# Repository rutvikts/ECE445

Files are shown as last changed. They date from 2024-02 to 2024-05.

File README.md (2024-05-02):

# ECE 445
UIUC ECE 445 - Senior Design Project Repository

# Project Details
## Oxygen Delivery Robot

Team Members:
- Rutvik Sayankar (rutviks2@illinois.edu)
- Aidan Dunican (dunican2@illinois.edu)
- Nazar Kalyniouk (nazark2@illinois.edu)

## Problem

Children's interstitial and diffuse lung disease (ChILD) is a collection of diseases or disorders. These diseases cause a thickening of the interstitium (the tissue that extends throughout the lungs) due to scarring, inflammation, or fluid buildup. This eventually affects a patient’s ability to breathe and distribute enough oxygen to the blood.

Numerous children experience the impact of this situation, requiring supplemental oxygen for their daily activities. It hampers the mobility and freedom of young infants, diminishing their growth and confidence. Moreover, parents face an increased burden, not only caring for their child but also being directly involved in managing the oxygen tank as their child moves around.

## Solution

Mobile oxygen delivery is a mostly untapped market for users both elderly and young. This project details a prototype design for a mobile oxygen delivery robot. We utilize a three-wheeled omnidirectional drivetrain, ultra-wideband triangulation, computer vision, and a simple Roomba-style bumper system. We remove ourselves from the context of dealing with oxygen-related tubing as swivel solutions already exist and focus on the issue of creating a robot that can autonomously and efficiently move an oxygen tank around in an indoor space.

### Final Robot Design
<p align="center">
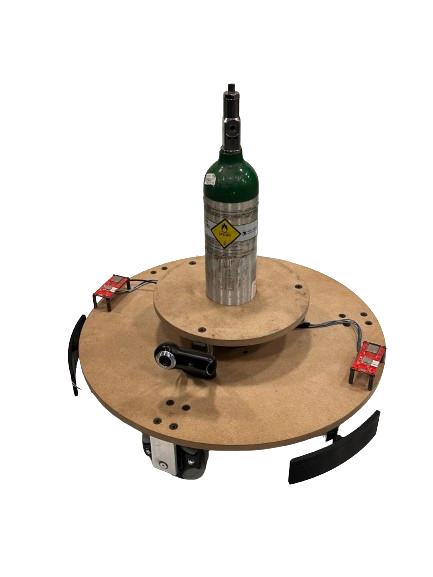
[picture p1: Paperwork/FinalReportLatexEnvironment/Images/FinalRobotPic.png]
  
</p>

### Final Robot Wiring (Underside)
<p align="center">
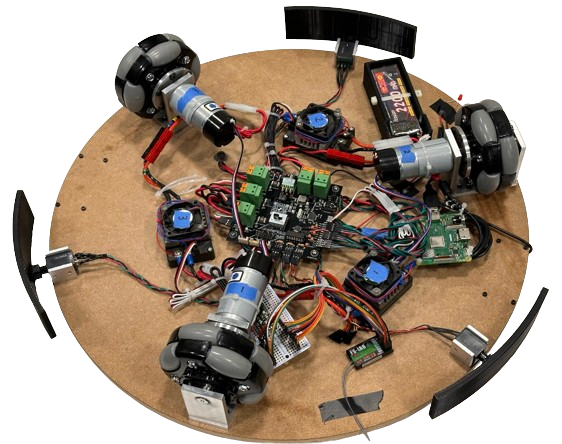
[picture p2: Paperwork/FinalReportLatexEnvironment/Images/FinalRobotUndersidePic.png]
  
</p>

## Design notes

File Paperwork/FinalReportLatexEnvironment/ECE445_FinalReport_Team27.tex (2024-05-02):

\documentclass{report}

\usepackage[top=1.5in,left=1.5in,bottom=1.5in,right=1.5in]{geometry}
\usepackage{amsmath}
\usepackage{bookmark}
\usepackage{listings} % for including nicely formatted code
\usepackage{array} % Included to solve invalid char in Tables declaration
\usepackage{graphicx} % to insert images
\graphicspath{{../pdf/}{/Users/rutviksayankar/Repos/ECE445_SP24/Paperwork/FinalReportLatexEnvironment/Images}} % setting up path for image storage

\usepackage{hyperref} % allows table of contents to be clickable to sections
\hypersetup{
    colorlinks,
    citecolor=blue,
    filecolor=blue,
    linkcolor=blue,
    urlcolor=blue
}

% Setting color formatting for Python code
\lstset{
    language=Python,
    frame=tb,
    basicstyle=\fontsize{8}{10}\ttfamily,
    keywordstyle=\color{blue},
    stringstyle=\color{red},
    commentstyle=\color{green},
    morecomment=[l][\color{magenta}]{\#},
}

% Setting color formatting for C code
\lstset{
    language=C,
    basicstyle=\fontsize{8}{10}\ttfamily,
    keywordstyle=\color{blue},
    stringstyle=\color{red},
    commentstyle=\color{magenta},
    morecomment=[l][\color{magenta}]{\#},
    frame=tb,
    numbers=left,
    % numberstyle=\tiny\color{gray},
    breaklines=true,
    showstringspaces=false,
}

% This section redefines the chapter headings, this allows us to remove the implicit "Chapter #" that comes before a provided chapter title.
\makeatletter
\def\@makechapterhead#1{%
  \vspace*{20\p@}%
  {\parindent \z@ \raggedright \normalfont
    \ifnum \c@secnumdepth >\m@ne
      %\if@mainmatter
        %\huge\bfseries \@chapapp\space \thechapter
        \Huge\bfseries \thechapter.\space%
        %\par\nobreak
        %\vskip 20\p@
      %\fi
    \fi
    \interlinepenalty\@M
    \Huge \bfseries #1\par\nobreak
    \vskip 40\p@
  }}
\makeatother

\title{ECE 445: Senior Design Project Laboratory \\ Final Report \\ Oxygen Delivery Robot} % Sets article title

\author {
    \textbf{Team 27} \\ 
    \textit{Sayankar, Rutvik}\\
    \textit{rutviks2@illinois.edu} \\
    \hfill \\ 
    \textit{Dunican, Aidan}\\
    \textit{dunican2@illinois.edu} \\
    \hfill \\ 
    \textit{Kalyniouk, Nazar}\\
    \textit{nazark2@illinois.edu} \\
    \hfill \\ 
    \textbf{Teaching Assistant} \\ 
    \textit{Subramaniam, Selva} \\
    \textit{ss170@illinois.edu} 
} 
\date{\today} % Sets date for date compiled

% The preamble ends with the command \begin{document}
\begin{document}
    \maketitle % creates title using information in preamble (title, author, date)

    \begin{abstract}
        Mobile oxygen delivery is a mostly untapped market for users both elderly and young. This report details a prototype design for a mobile oxygen delivery robot. We utilize a three wheeled omni-directional drivetrain, ultra wideband triangulation, computer vision, and a simple Roomba style bumper system. We remove ourselves from the context of dealing with oxygen related tubing as swivel solutions already exist and focus on the issue of creating a robot that can autonomously and efficiently move an oxygen tank around in an indoor space.
    \end{abstract}
    
    \pagebreak
    \tableofcontents % creates table of contents
    \pagebreak

    \chapter{Introduction}
    \section{Project Overview}
    Children's interstitial and diffuse lung disease (ChILD) is a collection of diseases or disorders. These diseases cause a thickening of the interstitium (the tissue that extends throughout the lungs) due to scarring, inflammation, or fluid buildup \cite{ChILD-2022}. This eventually affects a patient’s ability to breathe and distribute enough oxygen to the blood. Numerous children experience the impact of this situation, requiring supplemental oxygen for their daily activities. It hampers the mobility and freedom of young children, diminishing their growth and confidence. Moreover, parents face an increased burden, not only caring for their child but also having to be directly involved in managing the oxygen tank as their child moves around.

    Given the absence of relevant solutions in the current market, our project aims to ease the challenges faced by parents and provide young children the freedom to explore their surroundings without worry. As a proof of concept for an affordable solution, we propose a three wheeled omni-directional mobile robot capable of supporting a filled M-6 oxygen tank. We plan to implement two localization subsystems to ensure redundancy and enhance child safety. The first subsystem utilizes Ultra-Wideband (UWB) transceivers for triangulating the child's location relative to the robot in indoor environments, this is similar to how Apple AirTags triangulate their location relative to an iPhone \cite{airtag_uwb} (although AirTags use a combination of UWB and Bluetooth triangulation \cite{airtag_ble}). The second subsystem makes use of a desktop web camera which streams video to a Raspberry Pi where it will leverage open-source object tracking libraries to improve our directional accuracy in tracking a child. The final subsystems will focus on close range object detection.

    \newpage

    \section{Block Diagram}
    \begin{figure}[ht!]
      \centering
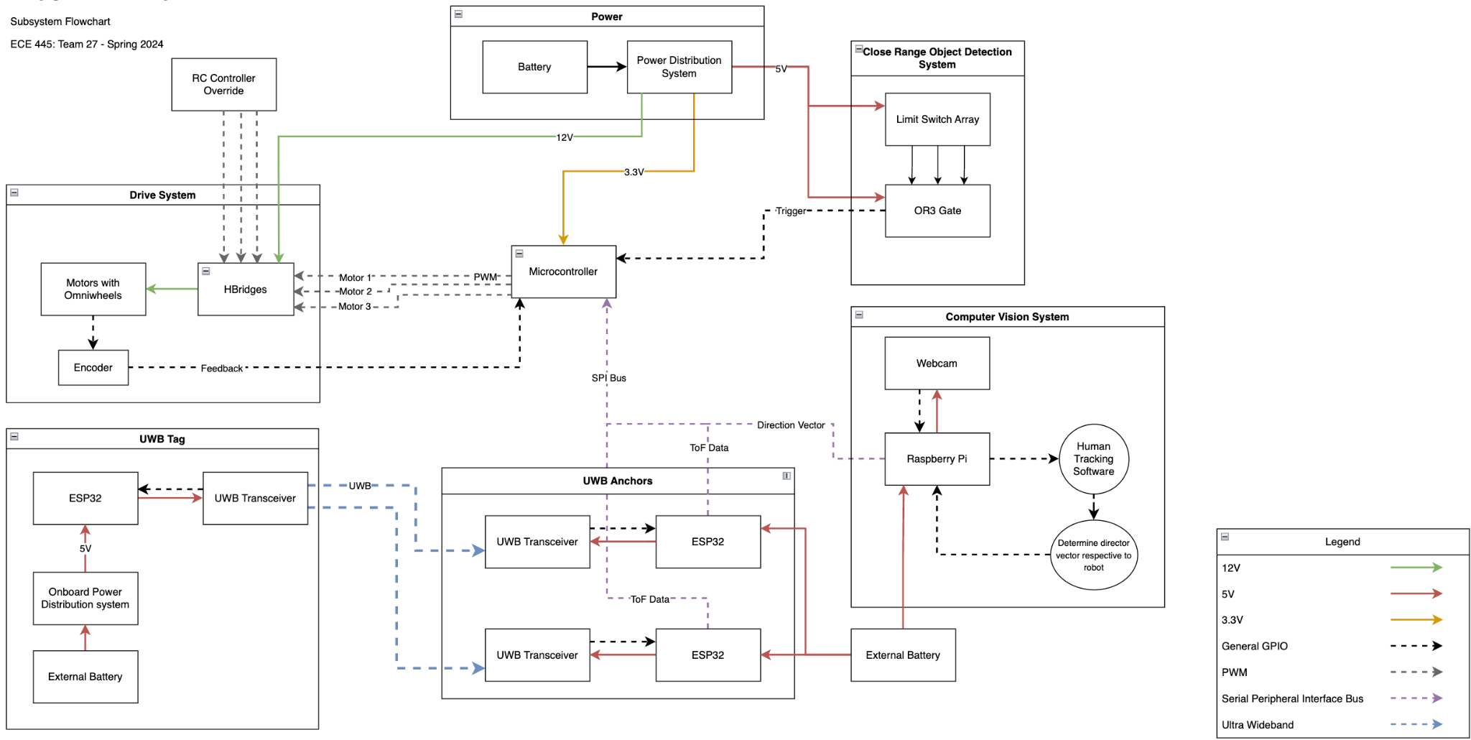
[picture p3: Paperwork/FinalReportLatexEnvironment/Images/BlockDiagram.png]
      
      \caption{High Level Block Diagram}
      \label{fig:BlockDiagram}
  \end{figure}

    \subsection{Omniwheel Drivetrain System}
    We utilize a three wheeled omni-directional wheel drive train. In software we make use of simple matrix multiplication (detailed in section \ref{sec:Omniwheel-InverseKinematics}) to derive individual wheel speeds given that we know where we want to go in Cartesian space.

    \subsection{Ultra-Wideband Triangulation System}
    This system makes use of UWB transceivers in order to triangulate location in an indoor space with high accuracy. The goal was to be able to locate the user in an indoor environment where there maybe be interference with other bluetooth or wifi signals. 
    
    \subsection{Close Range Object Detection System}
    The Close Range Object Detection subsystem makes use of limit switches with bumpers attached to them arranged in a ring around the robot that will detect when it encounters an object in its path. The goal of this system is to halt the robot and any further movement when a limit switch is pressed. This enhances the safety of the robot, particularly in environments with children. With the expectation that the robot will be utilized inside spaces such as a living room which might have toys scattered around due to younger children being present. To limit the scope of the project we want the robot to simply stop movement upon collision with any object in it's path and have either the user or a someone supervising come in and clear the area before the robot is to be used again.
    
    \subsection{Computer Vision System}
    The Computer Vision subsystem was incorporated into our design to ensure redundancy and robustness. By having a sensor fusion between this and the UWB subsystem, we can ensure that the robot follows the child as desired and add an extra layer of redundancy and safety to our design. The performance requirements of this subsystem are that this subsystem will initiate a corrective measure to the STM32 microcontroller if the child deviates too far from the center of the input frame. Specifically, this system focuses on the degrees away from the center the user currently is. Between the start of this design and the end, nothing was changed in the block level of this subsystem.
    
    \subsection{Control System}
    This system is purely regarding how the STM32 microcontroller interacts and controls all our peripheral devices.
    
    \subsection{Power System}
    The power system of our robot was designed to take a 12V input and regulate it down to the 5V and 3.3V rails that will be used by all devices on our PCB. Specifically, for our 3.3V rail we needed to ensure a clean supply as it would be powering our STM32 microcontroller, which will be generating all of our PWM signals and reading a lot of timer related signals for which a clean 3.3V is preferred.

    \chapter{Design}
    \section{Design Procedure}

    \subsection{Omniwheel Drivetrain System}
    \label{sec:Omniwheel-DesignProcedure}

    We utilize a three wheeled omni-directional wheel drive train. Chosen mainly due to the cost benefit over a similar four wheeled drive train. This type of system is susceptible to drift in the form of yaw, therefore we made sure to include feedback from encoders back into our STM32 microcontroller to allow for drift compensation.

    \subsection{Ultra-Wideband Triangulation System}
    Our initial design discussion was regarding the type of wireless indoor localization we want to design. Immediately, two types of communication came to mind: UWB and BLE. Ultimately, we chose UWB over BLE due to the following benefits:

    \begin{itemize}
      \item Data transmission: UWB can transmit more data than Bluetooth Low Energy
      \item Accuracy: UWB can more accurately measure distance and determine position because it uses wideband radio waves and higher frequency bands
      \item Interference resistance: UWB is less likely to be affected by interference and obstructions
    \end{itemize}

    \subsubsection{Localization Algorithms} 
    To break it down simply, our goal was to find out the location of a user relative to our robot. We assume the user and robot will be in a valid location in real world space, and therefore can just focus on the user's location relative to our robot.

    To localize the user, we need to create a triangle of known lengths with vertices defined by the UWB transceivers. To obtain the lengths of each side we need to perform some ranging between the tag transceiver (the transceiver which the user will have) and the anchor transceivers (which are mounted onto the robot). With the anchors being a set 18" apart (the minimum as required by the DW3000 ICs we were using), we only needed the remaining two sides of our triangle.

    There are two ways to range between UWB transceivers. The first is to use Time of Flight (ToF). ToF is a positioning method based on two-way ranging. That means the tag needs to send and receive signals from the anchor several times and then the flight time of the signal between the anchor and the tag can be measured, because radio waves travel at the speed of light, we can calculate the distance between the tag and each anchor given that we know how long it took for a signal to travel between them. Secondly, Time Difference of Arrival (TDoA) is localization based on comparing the time difference between signals and each anchor and this technique requires an accurate time synchronization function. When using the TDoA method, the UWB tag will send out a poll message, and all the nearby UWB anchors will receive it and record the arrival time. Because the location of anchors is different, they will not receive the message at the same time. We can use these time differences to determine the tag’s location.

    Implementing an accurate time synchronization function between all of our transceivers increases the complexity of the project ten-fold therefore we decided to use a ToF based ranging method to calculate the distance between each anchor and the tag device.
    
    \subsection{Close Range Object Detection System}

    This system is the simplest but definitely required some debate in terms of how we wanted it implemented. We debated between two main types of detection: simple limit switches or ultrasonic sensors. Limit switches don't require explanation, you activate a switch and a signal goes high. The only struggle here would be finding a limit switch that would be suitable for our needs. The alternative was ultrasonic detection which would have required us to use a much larger number of sensors and which would have been much more sensitive. The reason we decided to use limit switches was that they would only stop the robot when an object collides with it. In addition, limit switches allow us to make a 360-degree bumper for the robot with only 3 switches, which would fill in the gap between each wheel. To design the subsystem we decided to go with the 3 Honeywell 101SN11 limit switches as they were the best available limit switch in the ECE Self-service center (put simply, it was the only limit switch that could take any sort of impact without damage). One of the major issues we had when designing this subsystem was how to get the Honeywell limit switches to work. Seeing as these limit switches have since been discontinued, finding proper documentation on them proved to be difficult. We discovered that the output to the limit switches needed a 10k pull-up resistor in order to drive the output high when the limit switch is inactive. This was all thanks to a helpful ebay seller who provided a simple explanation on the function of some old limit switches he was selling (\url{www.ebay.com/itm/333999755279 }).
    
    \subsection{Computer Vision System}
    Alternate approaches to incorporating person detection besides using a Haar cascade which we ultimately chose are as follows.
    
    \begin{itemize}
      \item Histogram of Oriented Gradients (HOG)
      \item You Only Look Once (YOLO)
      \item Single Shot MultiBox Detector (SSD)
    \end{itemize}
    
    Haar cascade was chosen for our final implementation as it is simpler to implement than conventional deep-learning models. It contains pre-trained full body models, a large stepping stone which would be required for our project. For the Haar cascade algorithm, a pre-trained model that detects full bodies is used. Once the body is detected, a bounding box is drawn around the body. The center point of this box and the center point of the screen are compared and this determines how far off the center the body is.
    
    \subsection{Control System}

    The details of the control system during design were fairly simple. It mainly consisted of choosing a microcontroller and deciding what pins to assign where. We were limited by what was provided by the ECE supply center, we decided to go with the F103 line of STM32 chips as we believed it had the perfect amount of GPIO and timer pins required for our robot. Our final pin assignments are shown in figure \ref{fig:STM32Pinout}.
    \\
    \\
    We required individual timers for the following:
    \begin{itemize}
      \item PWM output to motors (can all be synchronized therefore only need one timer)
      \item Motor 1 Encoder feedback
      \item Motor 2 Encoder feedback
      \item Motor 3 Encoder feedback
    \end{itemize}
We required GPIO for the following:

    \begin{itemize}
      \item Limit switch bumper input
      \item USB lines
      \item SPI bus
      \item Chip select for 3 peripherals on the SPI bus
      \item High Speed External Crystal Oscillator input and output.
      \item Programmer pins
    \end{itemize}
    
    \subsection{Power System}

    In our initial power design we had four requirements:

    \begin{itemize}
      \item Supply a max of $9~A$ at $12~V$ per motor therefore $27~A$ at $12~V$
      \item Supply $5~V$ to supply around $3.5~A$ line to power items like a Raspberry Pi running computer vision software, and two ESP32 boards that power the UWB transceiver anchors on the robot, and some other miscellaneous 5V powered ICs throughout our PCB.
      \item Supply $3.3~V$ at $< 80~mA$ for our STM32.
    \end{itemize}

    We initially began with separate buck converters for each of our power rails. This original design took up lots of space on our PCB and was unnecessary as we only needed one $5~V$ line rated for higher current. After realizing that our selection of ESP32 boards and Raspberry Pi's do not have the option of power delivery through GPIO pins, we decided to use an external battery pack to supply them power. But we opted to leave our higher current buck converter in the design to leave headroom for the possibility of delivering power to our Raspberry Pi and two ESP32 boards in the future. This led us to designing our final power system which consisted of a $12~V$ to $5~V$ buck converter rated for up to $6~A$. This was followed with a $5~V$ to $3.3~V$ LDO to supply the power to our $3.3~V$ line. The reason we opted to go with an LDO for the 3.3v was because it was supplying power to the microcontroller which due to its sensitivity needed to be at a stable $3.3~V$ ideally without much noise. By opting to go with an LDO we were able to lower the noise floor and improve the line regulation of the supply going to the STM32 and hopefully improve the analog performance of our microcontroller.

    To further ensure the performance of the our analog pins in our microcontroller we decided to make use a ferrite bead which suppresses high-frequency electronic noise in electronic circuits. Ferrite beads employ high-frequency current dissipation in a ferrite ceramic to build high-frequency noise suppression devices.

    \section{Design Details}

    \subsection{Omniwheel Drivetrain System}
    \subsubsection{Inverse Kinematics of the OWB}
    \label{sec:Omniwheel-InverseKinematics}
    In a three-wheeled omni-wheel robot, the three wheels are arranged in a triangular pattern, with one wheel at the front and two wheels at the back. Each wheel has several small omni-directional wheels arranged in a circular pattern, which allows the robot to move in any direction.
    
    To move the robot, each wheel is driven independently using a motor. By varying the speed and direction of each wheel, the robot can move in any direction and rotate around its center point.
    
    The kinematics of a three-wheeled omni-wheel robot can be modeled mathematically the below equations \cite{riky2021omnidirectional} which relate the robot's linear and angular velocities to the speed and direction of each wheel.
    
    We first define for each wheel a direction of rotation $V_i$, and the resulting movement effected in the x and y axes, $V_ix$ and $V_iy$ as shown below.

    Knowing the angle of each wheel from the vertical axis, we can compute the x and y components created by the rotation of each wheel. By summing these components together, we can get the effective motion of the robot in the x, y and yaw axes.
    
    \[
    \begin{pmatrix}
    V_x \\
    V_y \\
    \omega
    \end{pmatrix}
    =
    \begin{pmatrix}
    1 & - \frac{1}{2} & -\frac{1}{2} \\
    0 & -\frac{\sqrt{3}}{2} & \frac{\sqrt{3}}{2} \\
    1 & 1 & 1
    \end{pmatrix}
    \begin{pmatrix}
    V_1 \\
    V_2 \\
    V_3
    \end{pmatrix}
    \]
        
    $V_{x}$ and $V_{y}$ are the desired linear velocities in the x and y directions, respectively, and omega is the desired angular velocity. $V_{1}$, $V_{2}$, and $V_{3}$ are the velocities of the three wheels, and L is the distance between the robot's center of mass and the wheel axes.

    \[
    \begin{pmatrix}
    V_1 \\
    V_2 \\
    V_3
    \end{pmatrix}
    =
    \begin{pmatrix}
    1 & - \frac{1}{2} & -\frac{1}{2} \\
    0 & -\frac{\sqrt{3}}{2} & \frac{\sqrt{3}}{2} \\
    1 & 1 & 1
    \end{pmatrix}^{-1}
    \begin{pmatrix}
    V_x \\
    V_y \\
    \omega
    \end{pmatrix}
    \]

    By taking the inverse of our 3x3 component coefficient matrix above, we can solve for our individual motor speeds $V_1$, $V_2$ and $V_3$, given the desired motion in terms of $V_x$, $V_y$, and $w$.

    \subsection{RC Control}
    For drivetrain testing and part of our demo we used an RC controller. We made use of a Flysky FS-i6 6CH 2.4GHz Radio System RC Transmitter Controller with FS-iA6 Receiver (\ref{fig:RCController}). While the receiver supports up to six channels, the OWB only needs three channels. 

    The OWB can move forward and backward like a normal RC car. This motion is represented by $V_y$, and is mapped to CH1 on the transmitter. While a normal RC car needs a $V_y$ component to turn left or right, the OWB can "yaw" on the spot. This is represented by $w$, and is mapped to CH3 on the transmitter. The final unique motion the OWB can execute is a "drift" toward the left or right. This motion is represented by $V_x$ and is mapped to CH2 on the transmitter.

    Thus, using these three channels, the operator can define the robot's desired $V_x$, $V_y$, and $w$. These desired motion vectors are then fed to our inverse kinematics algorithm, which breaks down our desired motion into an individual wheel speed and direction for each motor.

    \subsection{Ultra-Wideband Triangulation System}

    The UWB triangulation utilizing double sided two way ranging between the tag device which will be attached to the user. This tag will performing this ranging calculation with each tag device, therefore deriving the lengths of each side of our localization triangle.

    \subsubsection{Symmetrical double-sided two-way ranging}
    Symmetrical double-sided two-way ranging (SDS-TWR) is a ranging method that uses two delays that naturally occur in signal transmission to determine the range between two stations \cite{IEEE_802}.

    \subsubsection{Signal Propagation Delay}
    When a test packet is transmitted from station A to station B, the propagation delay can be calculated. As the packet travels through space, the difference in time is calculated from when it's sent from the transmitter to the receiver. This time delay is known as the signal propagation delay.

    \subsubsection{Processing Delay}
    Following the transmission between station A and station B, station A waits for an acknowledgement from station B. Once station A takes a known amount of time to process the test packet, it generates an acknowledgement and prepares it for transmission. The time it requires to process the acknowledged message is referred to as the processing delay.

    \subsubsection{Range Calculation}
    The signal propagation delay and the processing delay are encapsulated in the acknowledgment sent back to station A. On this acknowledgment, station A computes another signal propagation delay. These three values are then used by the algorithm to calculate the range between station A and station B.

    \subsubsection{Verifying Range Calculation}
    To verify the accuracy of the previous range calculation, station B sends a test packet to station A and station A sends an acknowledgement to station B once it receives the signal. By repeating this procedure, the two range values are determined and an average can be calculated to verify the accuracy of the distance measurement between these two stations

    \subsection{Close Range Object Detection System}
    Once the Honeywell 101SN11 limit switch is pressed it drives the output voltage low. This signal is pulled high with a $10~k \Omega$ resistor (refer to figure \ref{fig:limitswitchcircuit}). Then fed directly to the CD74HC00N four channel two input NAND gate in order to invert the signal to high when the switch is pressed. From there the 3 inverted limit switch signals are passed on to a 3 input OR gate which combines the inputs into one single output, which is high when any limit switch is pressed. Next the output is passed to the one of the STM32's FT ($5~V$ tolerant) pins and which triggers an interrupt that will stop the PWM signals that drive the motors from being generated. This in turn halts the motors placing the robot in an idle state until the limit switch is unpressed and the robot is reset.

    \subsection{Computer Vision System}
    For the software portion of this subsystem, the OpenCV code was written. Figure \ref{fig:Flowchart} provides an overview of how the algorithm works.

    To test the pre-trained Haar cascade classifier, the code was tested with an input image of a child walking down a hallway.

    When the body is detected, the distance is found between the center of the body and the center of the image. A distance is calculated by subtracting the two center points and dividing that number by the number of pixels on the screen. A message will be printed to inform the user if the off-center variable is large enough to where a correction will be needed. If no person is detected, a message will be printed. If this value is larger than $9\%$, a correction will be made. This initial calculator can be seen below. Later testing with the webcam will confirm whether this value is reasonable or will need to be adjusted. Some helpful design parameters regarding this calculation are as follows:

    \begin{itemize}
      \item Resolution of Camera = $1600 * 1200$ pixels
      \item FOV of Camera = $75$ degrees
      \item $\text{Average Shoulder Width of Child} = 9~\text{inches} = 0.23~m$
    \end{itemize}

    We expect the child will be a distance of $1~m \pm 25\%$ ($0.75~m \text{ to } 1.25~m$) away from the robot. Figure \ref{fig:redboxes} is an image of the minimum and maximum ranges. The red boxes are used to represent the width of the child. To calculate how much of the screen the child will take up, we must first calculate the horizontal width of the FOV \ref{fig:angle}. This is done by using simple trigonometry.

    Calculating horizontal FOV width:
    \begin{equation}
        \text{Half of FOV} = (\frac{75^\circ}{2} = 37.5^\circ )
      \nonumber
    \end{equation}

    \begin{equation}
      x = (1~\text{meter}) \times \tan(37.5^\circ) = 0.767~\text{meters}
    \nonumber
    \end{equation}

  Now, multiply this distance by 2, and the result is the horizontal FOV width.

  Horizontal FOV Width = $0.767 \text{ meters} \times 2 = 1.534 \text{ meters}$ 

  Now to calculate how much of the screen the target takes up with the current values.
  
  \begin{equation}
    \text{Percent of screen} = \frac{\text{Average Shoulder Width of Child}}{\text{Horizontal FOV Width}} = 15\%
  \nonumber
  \end{equation}
  
Since we want to stay within this range, the tolerance for the Percent of Screen taken up by the child will be \(15\% \pm 3\%\). 
The center of the child and the center of the screen will be compared to determine if a correction will be made. Therefore, we divide \( 15\% \) by \( 2\% \) to get \( 7.5\% \) and add \( 1.5\% \) to that value, so if the difference between the two midpoints is more than \( 9\% \), then a correction will be made.

With input images working, we tested the code with a video input from the web camera. Using similar code as before, it was modified to capture frames from a live video stream. First, we used a MacBook Pro web camera as we tested our code in a jupyter notebook, then went on to use the Logic Pro 9000 web camera. Similar to before, when a full body is detected, a bounding box is drawn around the person. The offset was calculated and printed on the screen. 

This code was modified further to ensure that there are no error detections. This was done by checking for the largest body in the frame so that no accidental object in the background would be flagged as a body. This greatly increased the accuracy of the detection and helped to only draw a bounding box around the body. 

Originally, our intention was to flash an SD card with an operating system to download OpenCV on a Raspberry Pi 3 Model B. However, we encountered difficulties when attempting to boot it. Despite multiple troubleshooting attempts, this issue persisted so we opted to utilize a spare Raspberry Pi 3 Model A+. This model was compatible with the flashed SD card and allowed us to continue. While this issue was resolved, issues arose when trying to download OpenCV. Since this was a slightly older model than the previous Raspberry Pi, the limited RAM struggled to download OpenCV since it is very resource intensive. Due to time constraints and the fact that this wasn’t one of the high-level requirements, efforts were focused on ensuring our high-level requirements were met. In the future, a stronger Raspberry Pi, such as the Raspberry Pi 4, would be a better option. 

If OpenCV were to work on the Raspberry Pi, the next step would’ve been to set up communication between the Raspberry Pi and STM32 over SPI. Once communication was established, a sensor fusion of the computer vision and ultra-wideband sensors. This would ensure the desired child-tracking that we would want our omni wheel robot to exhibit.

    \subsection{Control System}

    The pinout of our STM32 was detailed in figure \ref{fig:STM32Pinout}. We implemented system interrupts as shown in figure \ref{fig:interrupt}.

    In order to setup our SPI bus we took a register setting approach. Therefore, we write and access registers directly to read SPI bus data, enable and write to the bus. 
    
    See figures \ref{fig:SPIConfig}, \ref{fig:SPI_Transmit}, \ref{fig:SPI_Receive}, \ref{fig:GPIOConfig} and \ref{fig:SPI_Enable} for a brief overview of the setup within the STMCubeIDE. Comments are also included within the code which help describe the process. You can also refer to figure \ref{fig:PWM} for detail on how the motor control through PWM was setup.

    \subsection{Power System}
    Our system is powered from a 2200mAh battery (which we later acknowledge was a limiting factor in our final performance). To prevent excessive current draw from our motors and ensure that we have a method in hardware that prevents the motors running at full power, we integrated $9~A$ PTC Resettable Fuses on each power line connected to a motor. PTC fuses are made of a material that increases its internal resistance as the temperature increases, therefore if we are drawing too much current we increase the resistance on the line and reduce the current being supplied to the motors. Once the current or high temperature is removed, the polymer cools and returns to its original state, restoring the fuse to a low-resistance state.
    
    From there the $12~V$ from the battery is stepped down to $5~V$ by our buck converter (\ref{fig:BuckConverter}). We opted to go for a $6~A$ buck converter in order to allow for the possibility of directly powering the Raspberry Pi and UWB subsystem from the board without needed a redesign of the power system.

    After the battery voltage is dropped down to $5~V$ it is dropped down again to $3.3~V$ through an LDO (\ref{fig:LDO}). This $3.3~V$ is used to power the STM32 which is the main processor of our robot. We chose to go with an LDO due to its lowered noise floor compared to a buck converter and better line regulation which will ensure that the voltage of the STM32 is kept constant and will not be affected by any supply noise that could result negatively impact our sensitive analog processing.

    Another helpful debugging feature of our power subsystem is the addition of a jumper connector that allows for us to choose how to supply $5~V$ to our board. This was added in order to allow us to be debug our microcontroller and any peripherals without needed to power the motors. We provided the option to select to supply $5~V$ from the $12~V$ to $5~V$ buck converter, an external $5~V$ source, or through the USB Micro B port that was included on the board.

    \chapter{Verification}

    \section{Omniwheel Drivetrain System}
    For our OWB drivetrain our goal was to reliably set the speed and control RPM of motors. Following that, we wanted to maintain speed of 3 MPH under full load.

    We could tell from our encoder feedback that we were able to control with RPM, and unfortunately without a bigger battery we couldn't test the max speed of the robot. But without a bigger battery we were able to clearly move the robot in a desired direction but not move over 3 MPH.

    \section{Ultra-Wideband Triangulation System}
    For the UWB triangulation our goal was to utilize ToF to create a triangle of known lengths with vertices defined by each UWB transceiver. We tested creating a large triangle and comparing the serial read out to the read world distances. We also tested closer distances with a ruler. For all of our verification we were within tolerance.
    
    \section{Close Range Object Detection System}
    In order to verify our close range object detection subsystem we included a test point on the output of the OR gate (\ref{fig:OR3TestPoint}) which allowed us to be able to check the voltage level going into the STM32 when the limit switches were pressed.
    
    \section{Computer Vision System}
    A requirement of the Computer Vision subsystem was to utilize OpenCV or OpenPose to determine the angle of the child respective of the robot. To verify this requirement, the Raspberry Pi must be plugged into the monitor and display the video feed with an overlaid box over the body. In addition to this overlay, a value would be shown to represent how far off the body is from the center of the screen. As seen in figure \ref{fig:CVVerification}, this verification is fulfilled therefore confirming that this requirement was successfully implemented.
    
    \section{Control System}
    When connecting all of our peripherals together while our STM timers are active and trying to control the motors, we run into some issues with our SPI bus. We occasionally skip bits, refer to figure \ref{fig:SPISkipping}.
    
    \section{Power System}
    In order to be able to appropriately test our power system we included test points attached at the output of each voltage line to make it easier for us to validate. Starting off with our $12~V$ line we receive a voltage that is around $12~V \pm 5\%$ which is clearly showing in the figure \ref{fig:12V}. 
    
    Next with our $5~V$ line we wanted to achieve a similar margin of $\pm 5\%$ which we were able to achieve as shown in figure \ref{fig:5V}.

    Lastly, we also had a test point for our $3.3~V$ line which similarly we wanted to have a margin of $\pm 5\%$ which was met with a significantly lower margin as seen in figure \ref{fig:3V}.

    \chapter{Costs}
    Labor costs for each team member is calculated with the following equation
    \begin{equation} \label{eq:cost}
    \text{Estimated hourly rate} * \text{actual hours spent} = \text{individual labor cost}
    \end{equation}
Given current ECE graduate pay, this cost comes out to
    \[\$44/hr * 137~hrs = \$6028/person \]
    \[\$6028/person * 3~\text{team members} = \$18084 \]
Labor costs for each the machine shop is calculated using equation \ref{eq:cost}. Estimating the average pay for the ECE machine shop worker, this cost comes out to
    \[\$60/hr * 40~hrs = \$2400 \]
With that in mind, the robot cost is roughly as follows.
  \begin{figure}[ht!]
    \begin{center}
      \begin{tabular}{ | m{23em} | m{4em} | m{5em} | } 
        \hline
        \textbf{Item} & \textbf{Quantity} & \textbf{Cost}  \\ 
        \hline
        \hline
        PCB BOM
        & 
        1
        &
        \$62.03
        \\ 
        \hline
        PCB Manufacturing
        & 
        1
        &
        \$40.38
        \\ 
        \hline
        3D Printed Parts
        &
        1
        &
        \$5
        \\
        \hline
        \href{https://www.andymark.com/products/4-in-duraomni-wheel}{Omni-Wheels}
        &
        3
        &
        \$78
        \\
        \hline
        \href{https://www.gobilda.com/modern-robotics-12vdc-motor/}{Modern\:Robotics 12VDC Motor}
        &
        3
        &
        \$44.97
        \\
        \hline
        \href{https://www.gobilda.com/4-pos-jst-ph-mh-fc-to-4-pos-jst-xh-mh-fc-adaptor-150mm-length/}{4-Pos JST PH to 4-Pos JST XH Adaptor (Encoders)}
        &
        4
        &
        \$11.56
        \\
        \hline
        \href{https://www.team358.org/files/programming/ControlSystem2015-2019/specs/217-2769-Victor888UserManual.pdf}{Victor 888 Speed Controller}
        &
        3
        &
        \$149.97
        \\
        \hline
        \href{https://www.amazon.com/Logitech-Internet-Camera-2-0-Megapixel-Resolution/dp/B000RZQZM0}{QuickCam Pro 9000 Webcam}
        &
        1
        &
        \$74.99
        \\
        \hline
        \href{https://www.makerfabs.com/esp32-uwb-dw3000.html}{ESP32UWB DW3000 (Ultra-Wideband transceiver)}
        &
        3
        &
        \$131.40
        \\
        \hline
        \href{https://vilros.com/products/raspberry-pi-4-model-b}{Raspberry\:Pi\:4\:1GB Model B}
        &
        1
        &
        \$35
        \\
        \hline
        Machine Shop Parts
        & 
        -
        &
        \$74
        \\ 
        \hline
        \textbf{Robot Subtotal}
        &
        -
        &
        \textbf{\$707.30}
        \\
        \hline
        Machine Shop Labor
        & 
        -
        &
        \$2400
        \\ 
        \hline
        Team Member Labor
        & 
        -
        &
        \$18084
        \\ 
        \hline
        \textbf{Total}
        &
        &
        \textbf{\$21191.30}
        \\
        \hline
      \end{tabular}
      \caption{ Cost Breakdown } 
          \label{fig:costbreakdown}
    \end{center}
  \end{figure}

    \chapter{Conclusions}

    This project has effectively fulfilled the high-level requirements we proposed at the beginning of the semester. Key successes include the drive train, the UWB localization, and close-range object detection. These objectives have been successfully achieved as outlined in the previous section's R \& V tables. Some challenges that we faced were the small battery size preventing a sufficient current supply for extended use, SPI bus timing was sometimes skipping bits and prevented reliable communication between peripherals, we would have liked to print a full 360-degree bumper if we have a larger 3D printer. Further work would include allocating more time for SPI bus debugging and choosing a larger battery.

    \section{Ethics and Safety}
    \subsection{Ethical Considerations}
    As we continue through the development of our project, we are unwavering in our dedication to abide by the ethical and safety principles outlined by the Association for Computing Machinery (ACM) and the Institute of Electrical and Electronics Engineers (IEEE). As we embark on this project, we pledge our commitment to adhere to these standards, ensuring that our actions and choices uphold the highest level of professionalism and integrity.

    As outlined in Section I of the IEEE Code of Ethics, we pledge to “uphold the highest standards of integrity, responsible behavior, and ethical conduct in professional activities” \cite{IEEE_2020}. We will prioritize safety in our design and adhere to ethical design practices. Educating the parents and caregivers about the robot’s use and limitations will allow for informed decision-making. Following relevant laws and regulations regarding this technology will also be a high priority.

    In the same Code of Ethics, outlined in Section III, we pledge to “strive to ensure this code is upheld by colleagues and co-workers” \cite{IEEE_2020}. We will support each other in ethical conduct and foster a culture of ethical behavior. Open communication will be established and encouraged to raise concerns and provide guidance to team members.

    \subsection{Safety Considerations}
    This project aligns with the safety principles outlined in the ACM Code of Ethics and Professional Conduct. Safety remains our number one priority and as outlined in Section 1.2 \cite{ACM_2018}, we will avoid negative consequences, especially when those consequences are significant and unjust. We will take careful consideration of potential impacts and minimize harm. In the context of this project, we will ensure that the robot’s design and operation prioritizes safety, especially to the children this product aims to assist. We will work to analyze potential risk and consider the robot’s mobility and interaction with its environment.

    As well as promoting safety, privacy is also a very important guideline that will be followed, which is outlined in Section 1.6. As professionals, we must safeguard the personal information of our users, especially if it involves children. As it relates to this project, we will ensure that no data will be collected and stored in an external location. Data collection will be minimized to only what is necessary for the robot to operate.

    One aspect of our project where safety must be considered is regarding the use of lithium batteries. We acknowledge the potential risks associated with the misuse of lithium batteries. We are committed to following the safety guidelines associated with the batteries we plan on using. More specifically, maintaining the battery’s temperature within the recommended range. Also, we are dedicated to the responsible disposal of batteries to ensure sustainability.

    Since we are incorporating motors into our design, we will deploy essential control systems to mitigate potential hazards such as collisions with the environment. Safe operation will be ensured with the use of sensors, vision systems, and warning systems.

    \chapter{Figures and Tables}

    \section{Inverse Kinematics}

    \begin{figure}[ht!]
      \centering
      \begin{minipage}[b]{0.45\linewidth}
        \centering
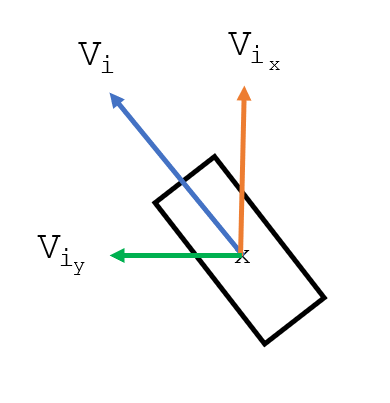
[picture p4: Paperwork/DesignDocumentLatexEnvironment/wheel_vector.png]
        
        \caption{Vector Definitions}
        \label{fig:vecdef}
      \end{minipage}
      \hfill
      \begin{minipage}[b]{0.45\linewidth}
        \centering
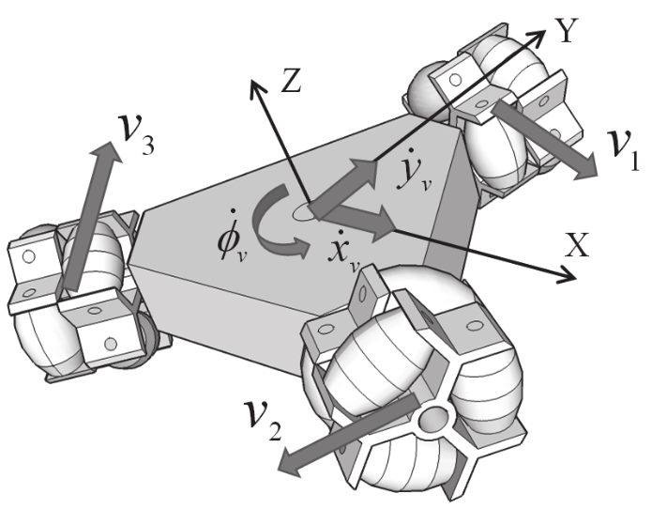
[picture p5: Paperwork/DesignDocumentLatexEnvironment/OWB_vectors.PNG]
        
        \caption{OWB drive vectors \cite{wada2015OWB}}
        \label{fig:owb_vec}
      \end{minipage}

      \label{fig:vecs}
    \end{figure}

    \newpage

    \section{Double-sided Two Way Ranging}

    \begin{figure}[ht!]
      \begin{center}
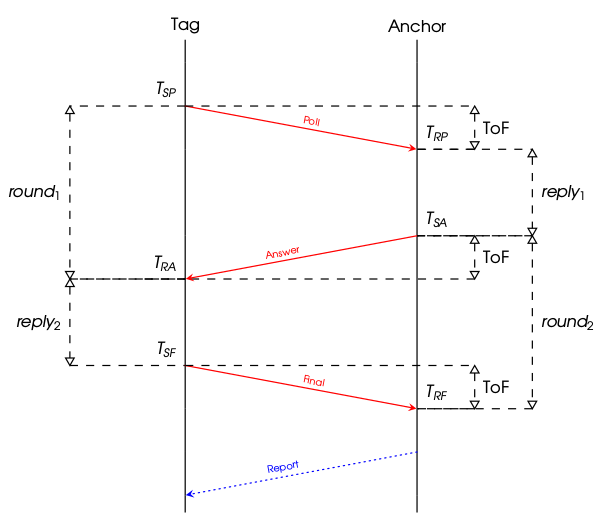
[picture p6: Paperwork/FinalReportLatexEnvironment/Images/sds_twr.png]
          \\
          \caption{ Symmetrical Double-sided Two-way Ranging } 
          \label{fig:sds_twr}
      \end{center}
    \end{figure}

    \newpage

    \section{Limit Switch Circuit}

    \begin{figure}[ht!]
      \begin{center}
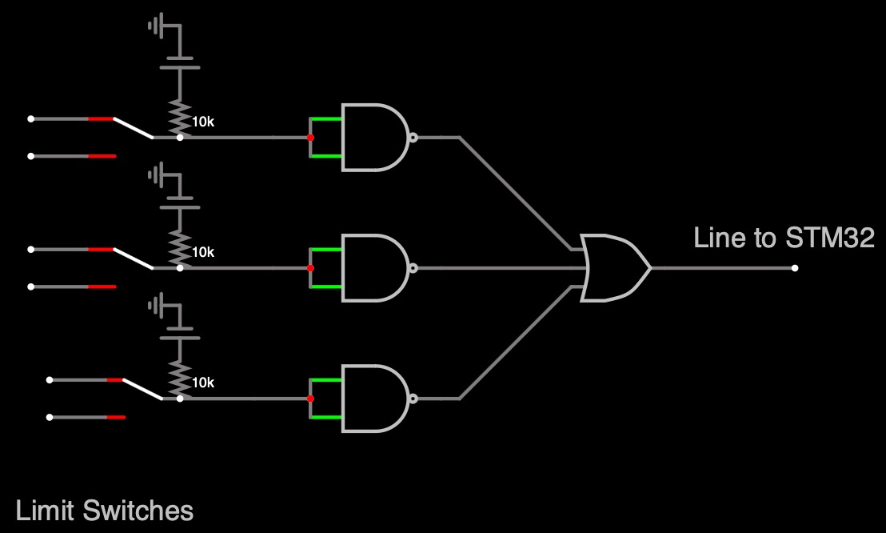
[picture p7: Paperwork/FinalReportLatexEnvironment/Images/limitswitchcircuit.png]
          \\
          \caption{ Limit Switch Circuit } 
          \label{fig:limitswitchcircuit}
      \end{center}
    \end{figure}

    \begin{figure}[ht!]
      \begin{center}
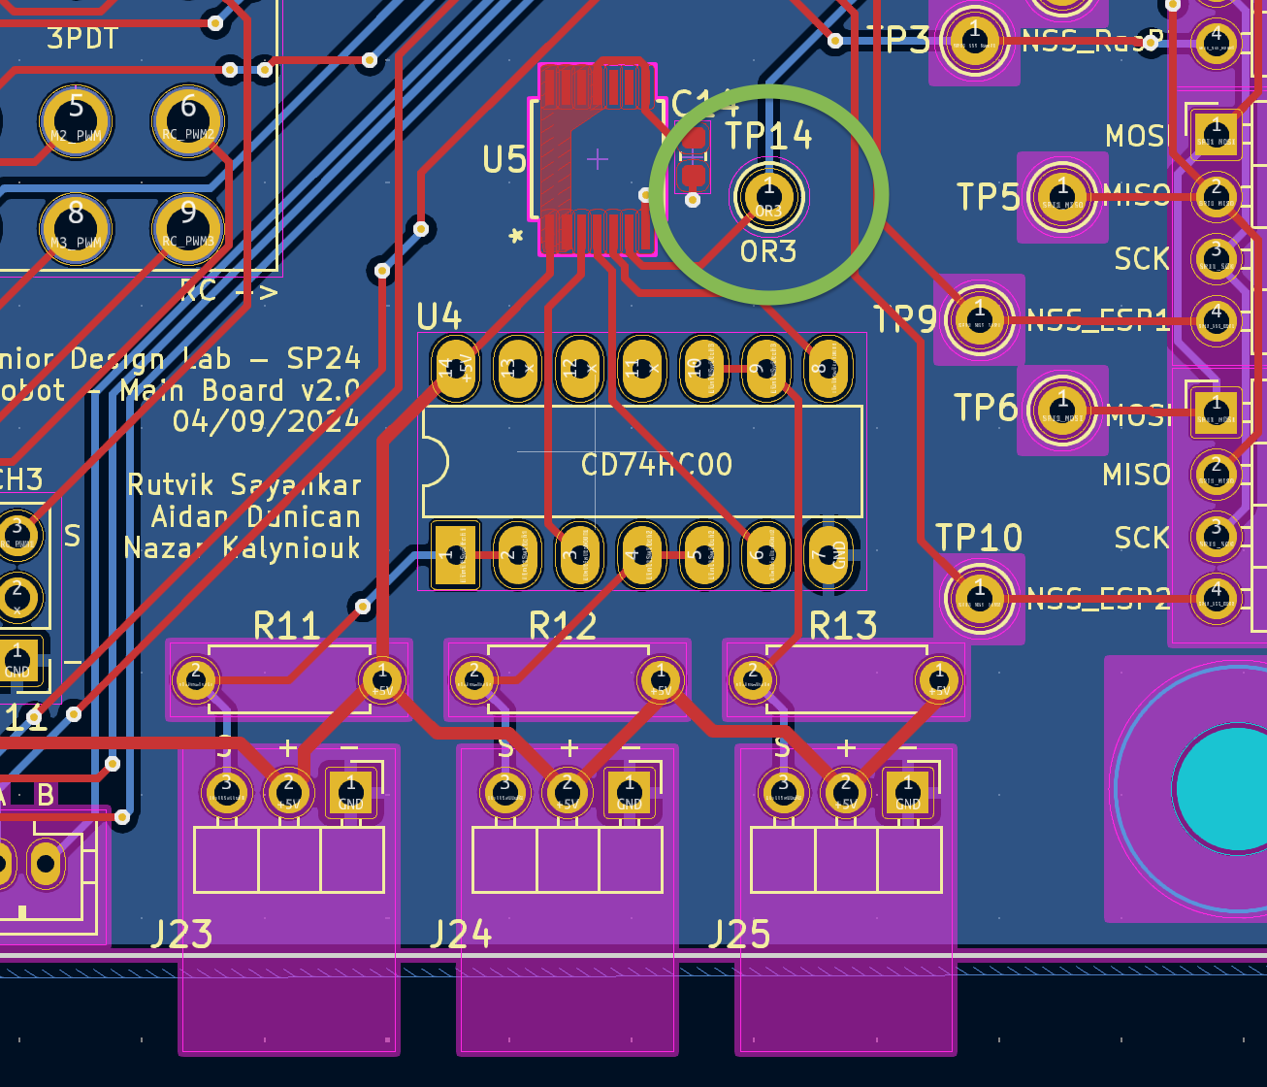
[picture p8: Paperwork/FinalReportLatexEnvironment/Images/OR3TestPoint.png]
          \\
          \caption{ PCB OR3 Test Point } 
          \label{fig:OR3TestPoint}
      \end{center}  
    \end{figure}

    \newpage

    \section{Open CV Images}

    \begin{figure}[ht!]
      \begin{center}
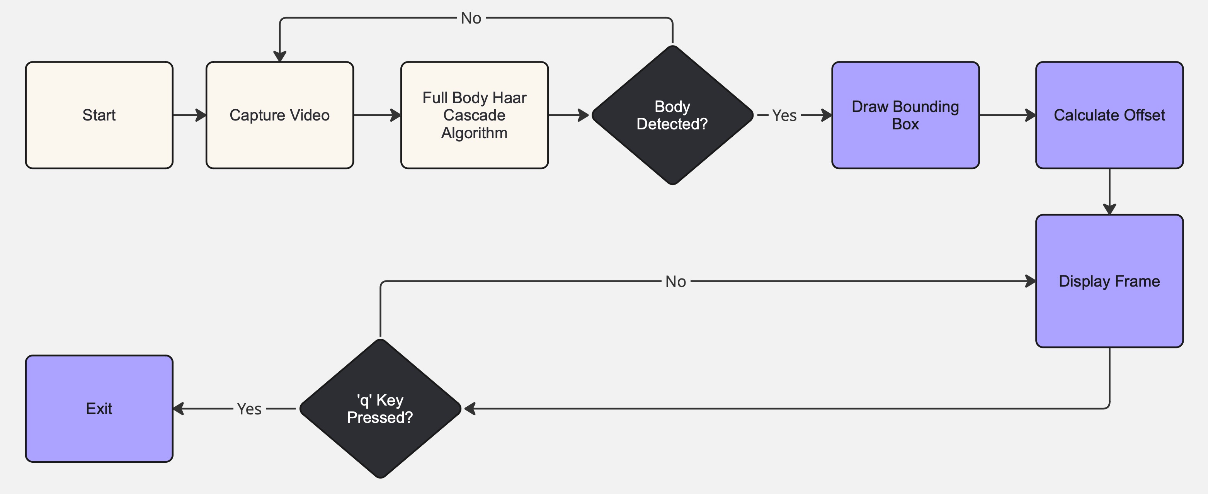
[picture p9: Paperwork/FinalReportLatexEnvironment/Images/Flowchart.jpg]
          \\
          \caption{ OpenCV Algorithm Flowchart  } 
          \label{fig:Flowchart}
      \end{center}
    \end{figure}

    \begin{figure}[ht!]
      \begin{center}
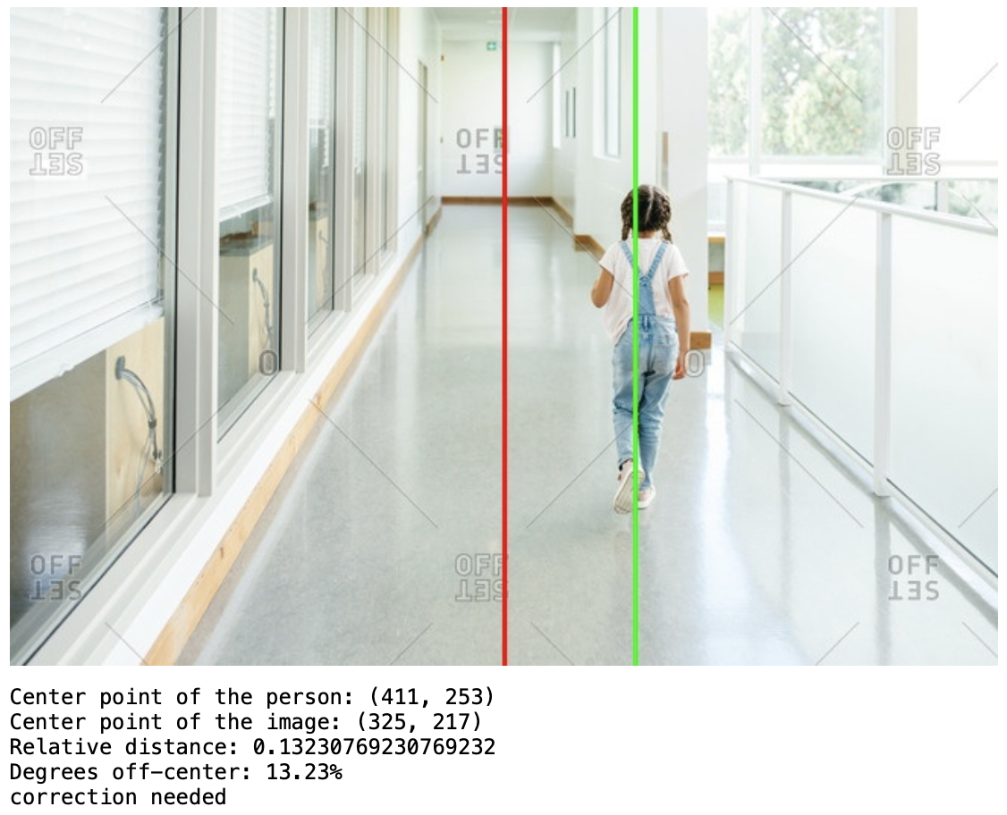
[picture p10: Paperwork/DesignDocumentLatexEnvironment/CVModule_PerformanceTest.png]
          \\
          \caption{ OpenCV Performance Test } 
          \label{fig:CVModule_PerformanceTest}
      \end{center}
    \end{figure}

    \begin{figure}[ht!]
      \centering
      \begin{minipage}[b]{0.45\linewidth}
        \centering
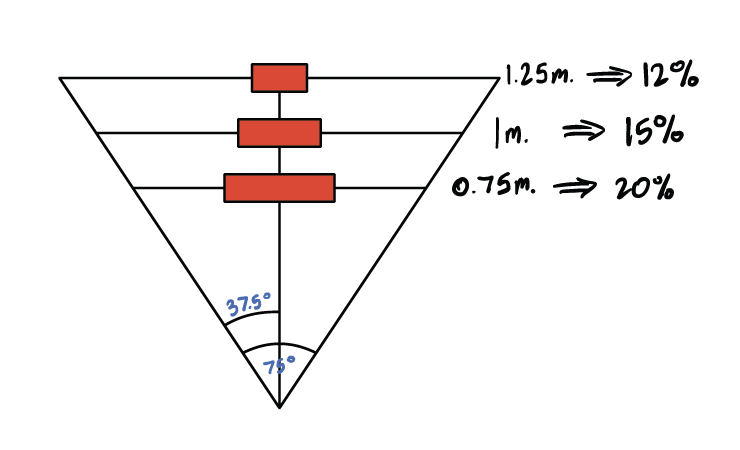
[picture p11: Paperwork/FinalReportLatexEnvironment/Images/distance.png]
        
        \caption{Percent of screen calculations for OpenCV algorithm}
        \label{fig:redboxes}
      \end{minipage}
      \hfill
      \begin{minipage}[b]{0.3\linewidth}
        \centering
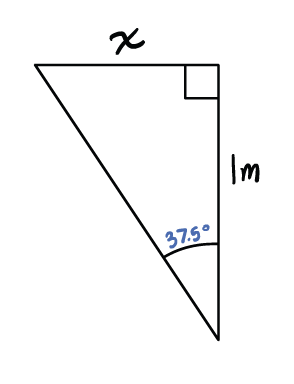
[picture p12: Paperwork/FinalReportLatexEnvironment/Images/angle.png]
        
        \caption{Calculation of Horizonatal FOV Width}
        \label{fig:angle}
      \end{minipage}
    \end{figure}

    \newpage

    \section{Power Delivery}

    \begin{figure}[ht!]
      \begin{center}
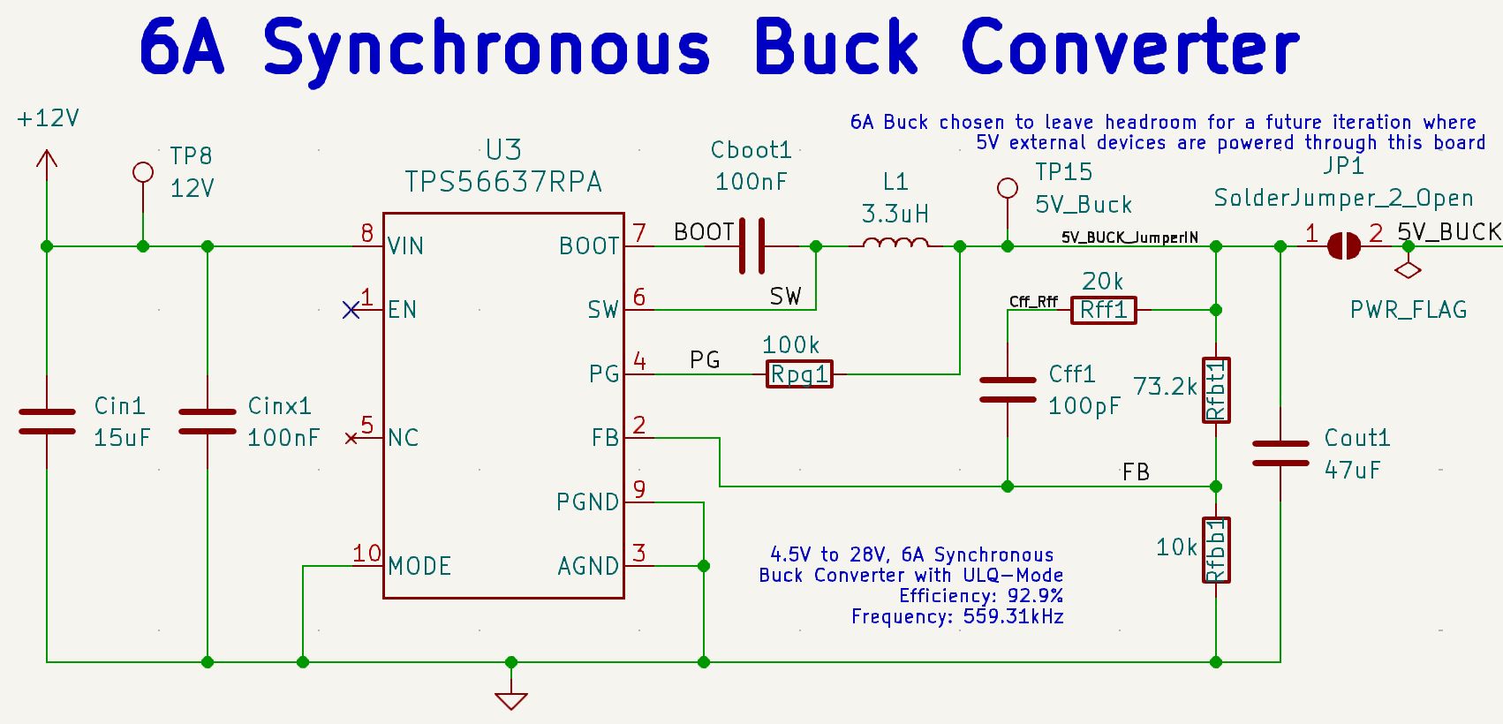
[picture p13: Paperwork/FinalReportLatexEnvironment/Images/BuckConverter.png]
          \\
          \caption{ $5~V$ $6~A$ Buck Converter } 
          \label{fig:BuckConverter}
      \end{center}
    \end{figure}

    \begin{figure}[ht!]
      \begin{center}
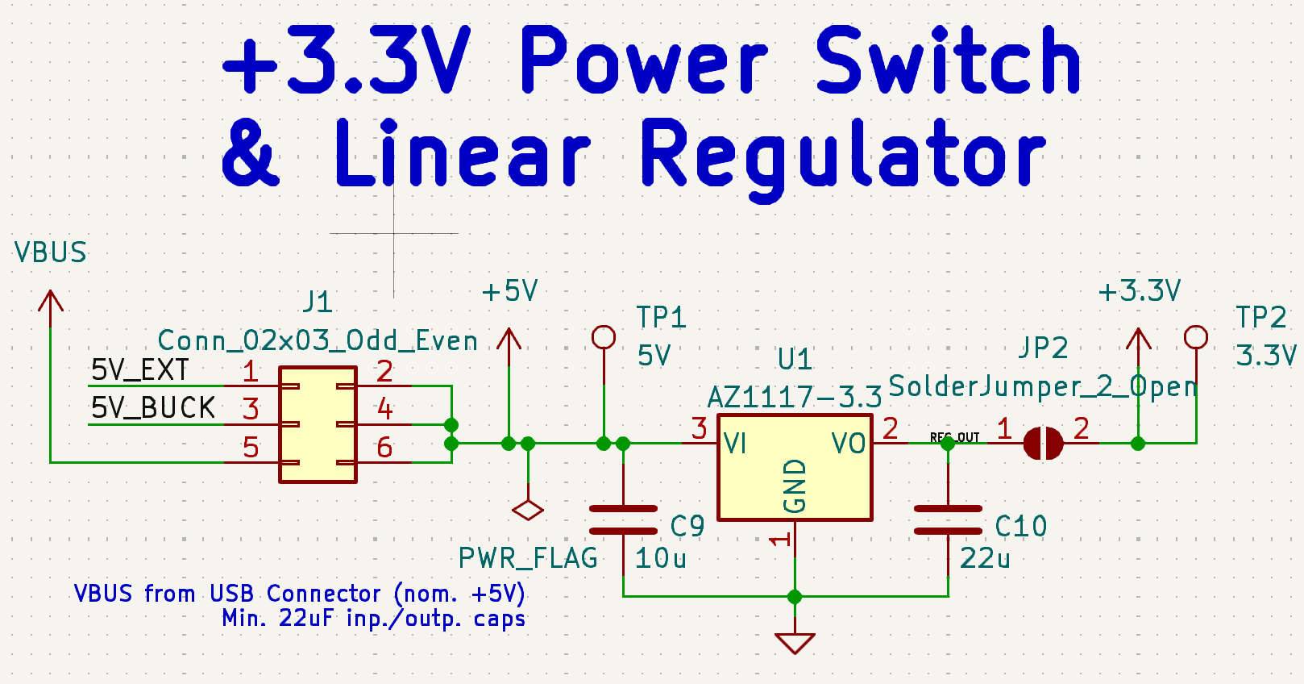
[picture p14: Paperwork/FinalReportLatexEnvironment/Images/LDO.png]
          \\
          \caption{ $3.3~V$ Low Dropout Regulator } 
          \label{fig:LDO}
      \end{center}
    \end{figure}

    \newpage

    \section{UWB Triangulation}

    \begin{figure}[ht!]
      \centering
      \begin{minipage}[b]{0.45\linewidth}
        \centering
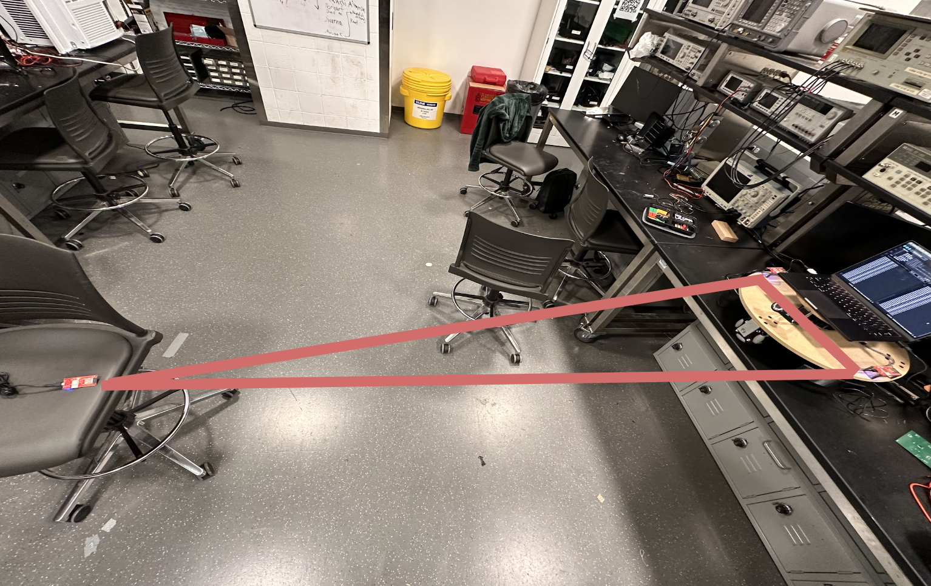
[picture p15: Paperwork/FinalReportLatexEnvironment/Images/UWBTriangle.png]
        
        \caption{UWB Triangle Laid out}
        \label{fig:UWBTriangle}
      \end{minipage}
      \hfill
      \begin{minipage}[b]{0.45\linewidth}
        \centering
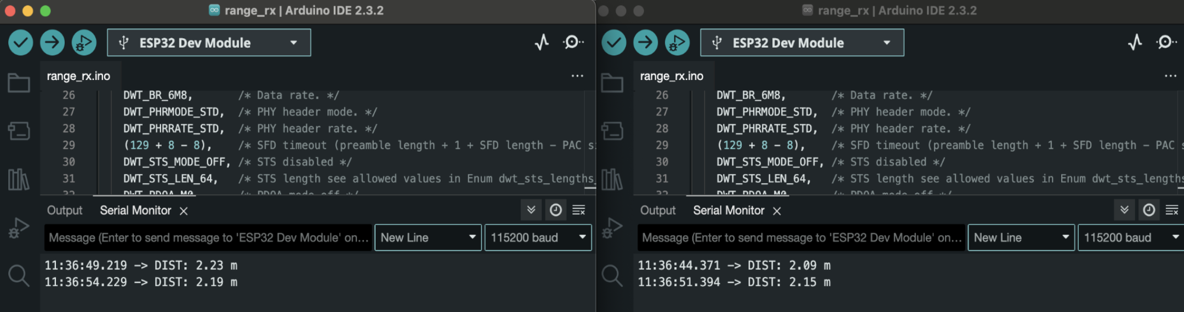
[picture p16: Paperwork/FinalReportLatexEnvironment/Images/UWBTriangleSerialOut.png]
        
        \caption{UWB Serial Read Out}
        \label{fig:UWBTriangleSerialOut}
      \end{minipage}
    \end{figure}

    \begin{figure}[ht!]
      \begin{center}
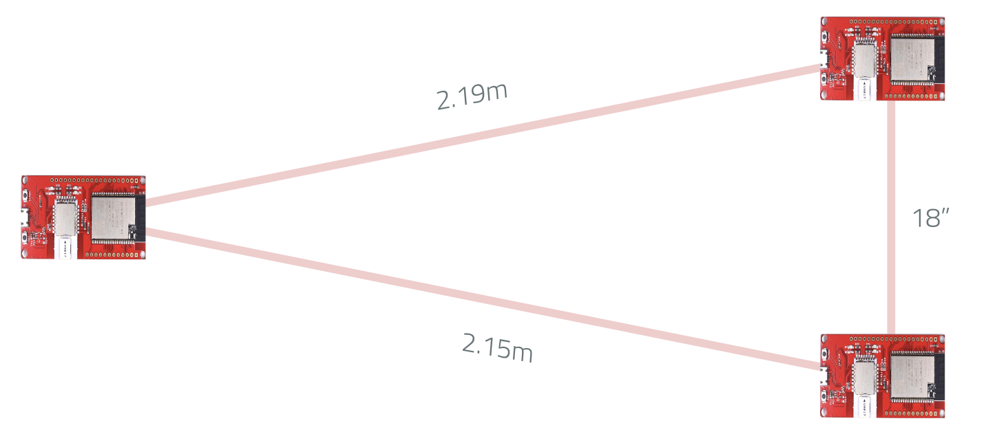
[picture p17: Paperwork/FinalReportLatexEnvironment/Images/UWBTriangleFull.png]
          \\
          \caption{ UWB Triangle with Distances } 
          \label{fig:UWBTriangleFull}
      \end{center}
    \end{figure}

    \begin{figure}[ht!]
      \centering
      \begin{minipage}[b]{0.45\linewidth}
        \centering
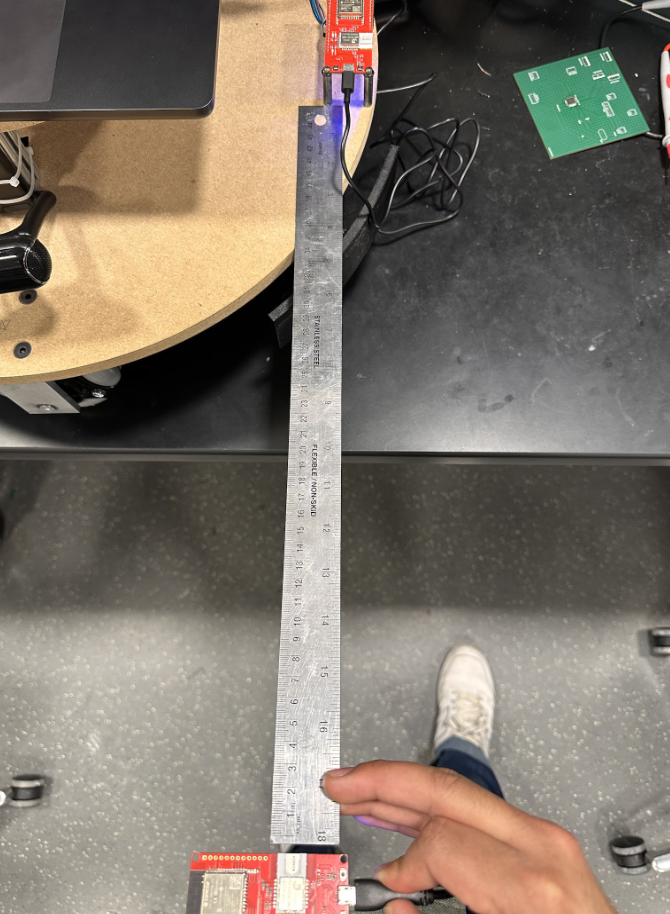
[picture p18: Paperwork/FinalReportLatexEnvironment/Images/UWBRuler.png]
        
        \caption{45" Ruler between UWB Transceiver}
        \label{fig:UWBRuler}
      \end{minipage}
      \hfill
      \begin{minipage}[b]{0.3\linewidth}
        \centering
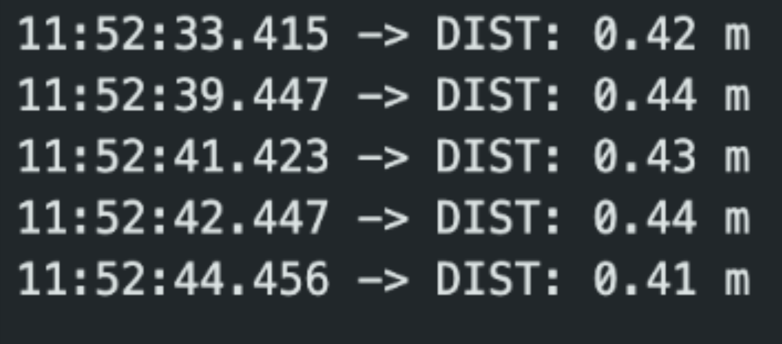
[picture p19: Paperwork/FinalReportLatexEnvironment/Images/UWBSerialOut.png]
        
        \caption{UWB Serial Read Out}
        \label{fig:UWBSerialOut}
      \end{minipage}
    \end{figure}

    \newpage

    \section{Computer Vision Verification}

    \begin{figure}[ht!]
      \begin{center}
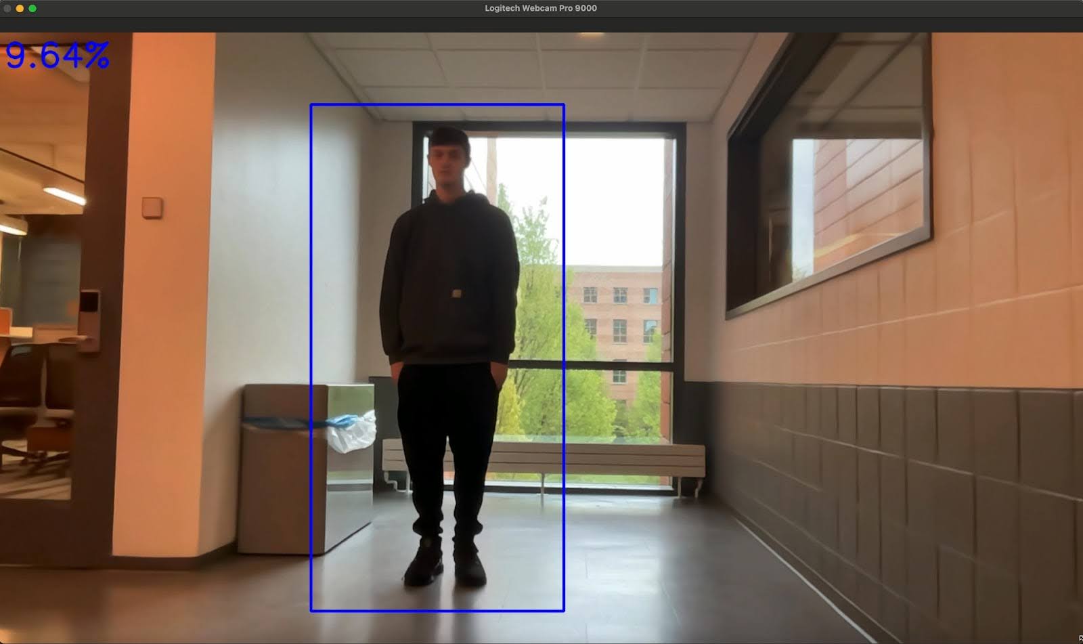
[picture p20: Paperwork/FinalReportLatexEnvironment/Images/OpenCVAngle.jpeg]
          \\
          \caption{ Computer Vision Verification } 
          \label{fig:CVVerification}
      \end{center}  
    \end{figure}

    \newpage

    \section{Control System Verification}

    \begin{figure}[ht!]
      \begin{center}
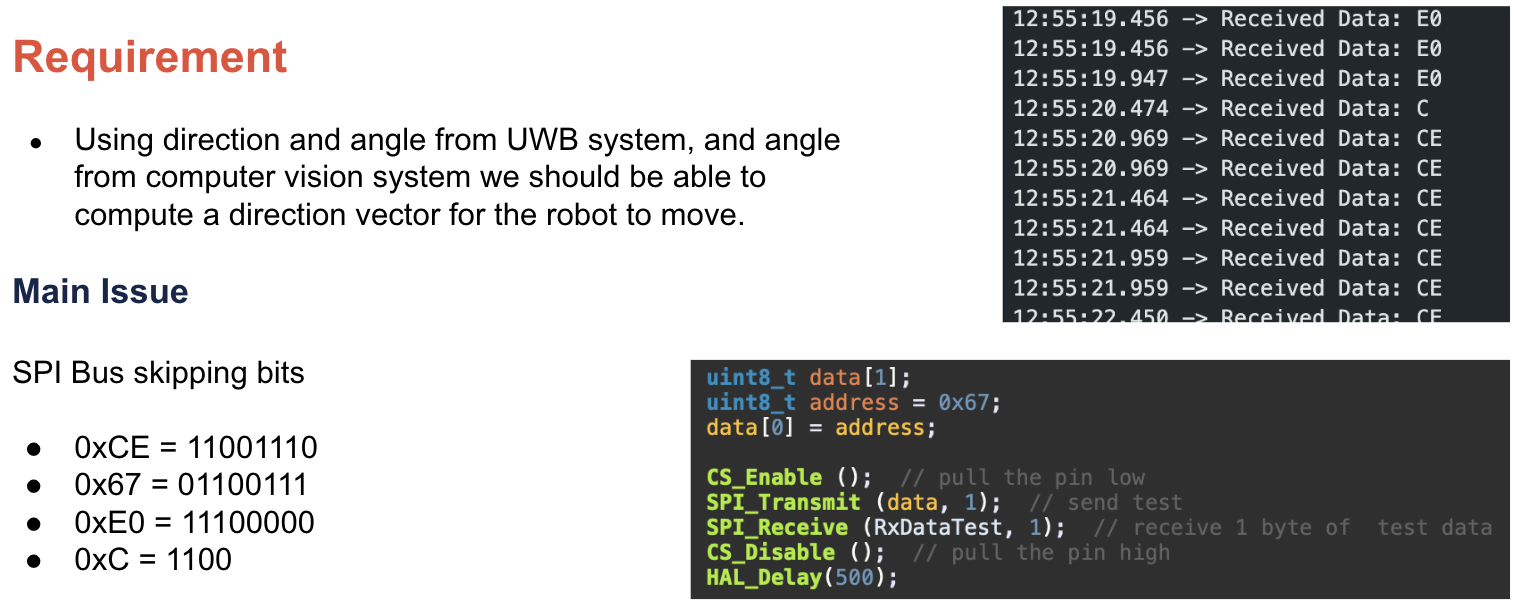
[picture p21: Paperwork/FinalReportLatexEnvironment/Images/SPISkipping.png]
          \\
          \caption{ SPI Bus Skipping Bits } 
          \label{fig:SPISkipping}
      \end{center}  
    \end{figure}

    \newpage

    \section{Power System Verification}

    \begin{figure}[ht!]
      \centering
      \begin{minipage}[b]{0.3\linewidth}
        \centering
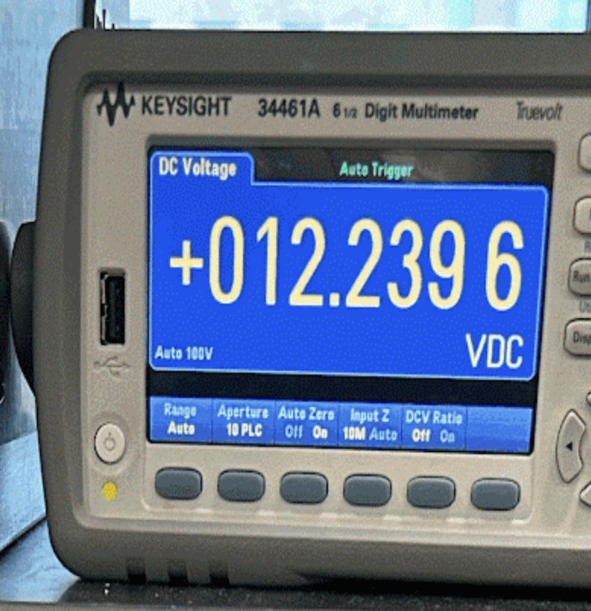
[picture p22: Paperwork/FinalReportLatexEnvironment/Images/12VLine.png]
        
        \caption{$12~V$ Power Line}
        \label{fig:12V}
      \end{minipage}
      \hfill
      \begin{minipage}[b]{0.3\linewidth}
        \centering
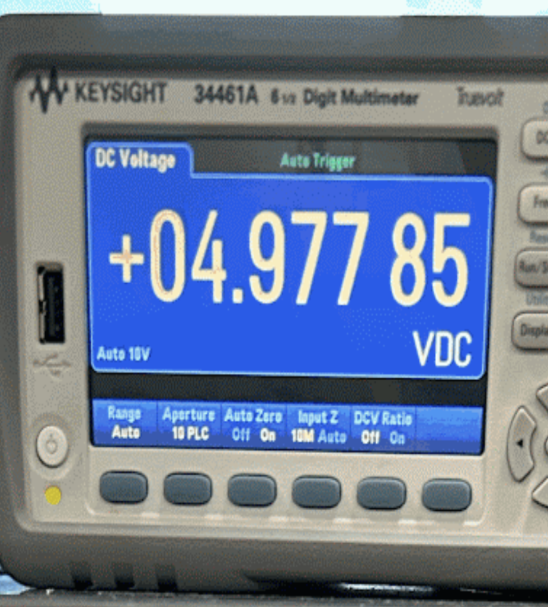
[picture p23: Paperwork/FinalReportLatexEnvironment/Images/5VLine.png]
        
        \caption{$5~V$ Power Line}
        \label{fig:5V}
      \end{minipage}
      \hfill
      \begin{minipage}[b]{0.3\linewidth}
        \centering
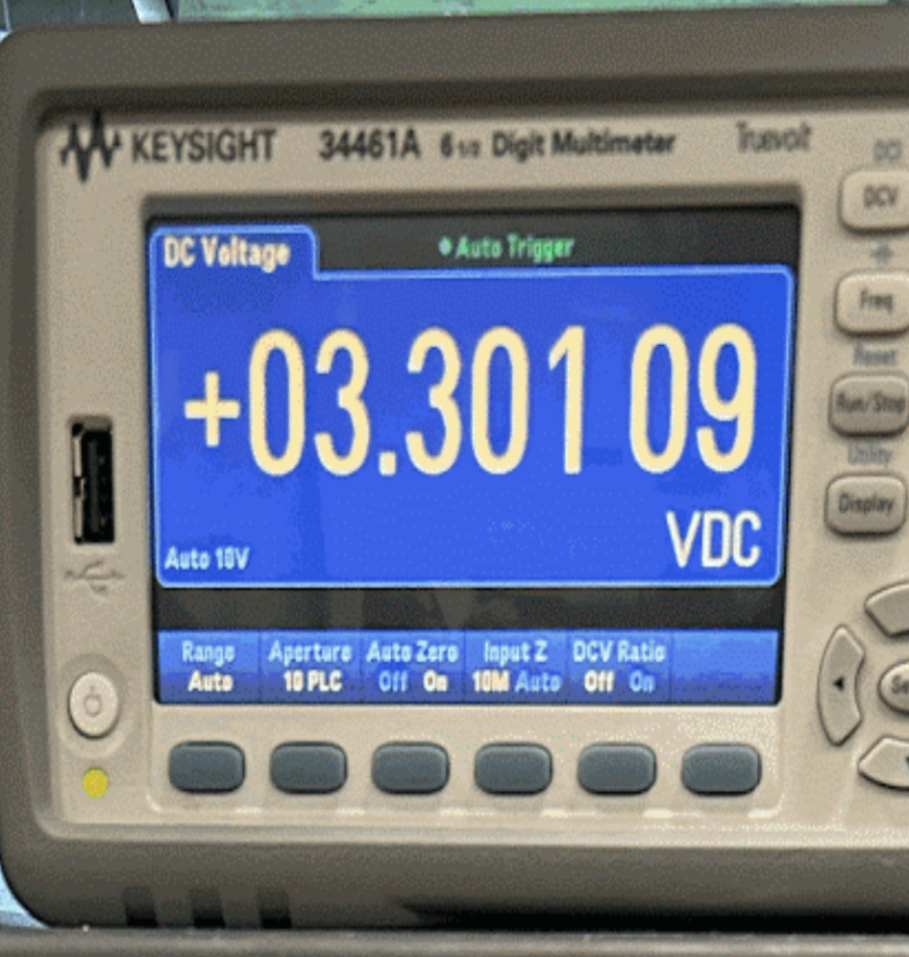
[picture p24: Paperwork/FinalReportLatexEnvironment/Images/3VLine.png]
        
        \caption{$3.3~V$ Power Line}
        \label{fig:3V}
      \end{minipage}
    \end{figure}

    \newpage

    \section{RC Controller}
    \begin{figure}[ht!]
      \begin{center}
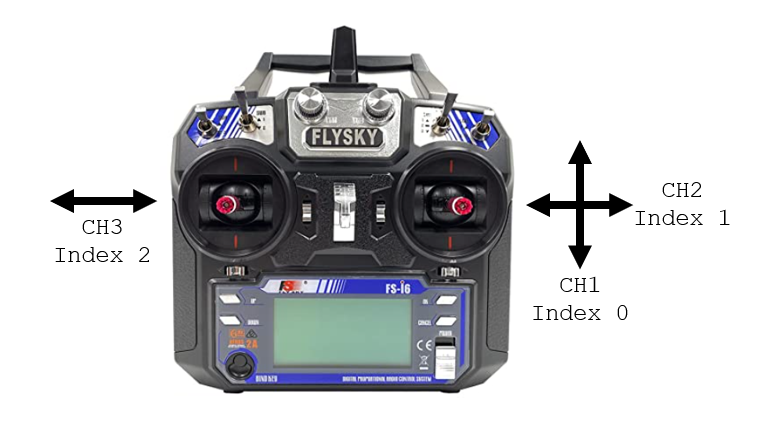
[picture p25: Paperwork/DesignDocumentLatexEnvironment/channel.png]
          \\
          \caption{ Channel Distribution  } 
          \label{fig:RCController}
      \end{center}
    \end{figure}

    \newpage

    \section{STM32 Pinout}

    \begin{figure}[ht!]
      \begin{center}
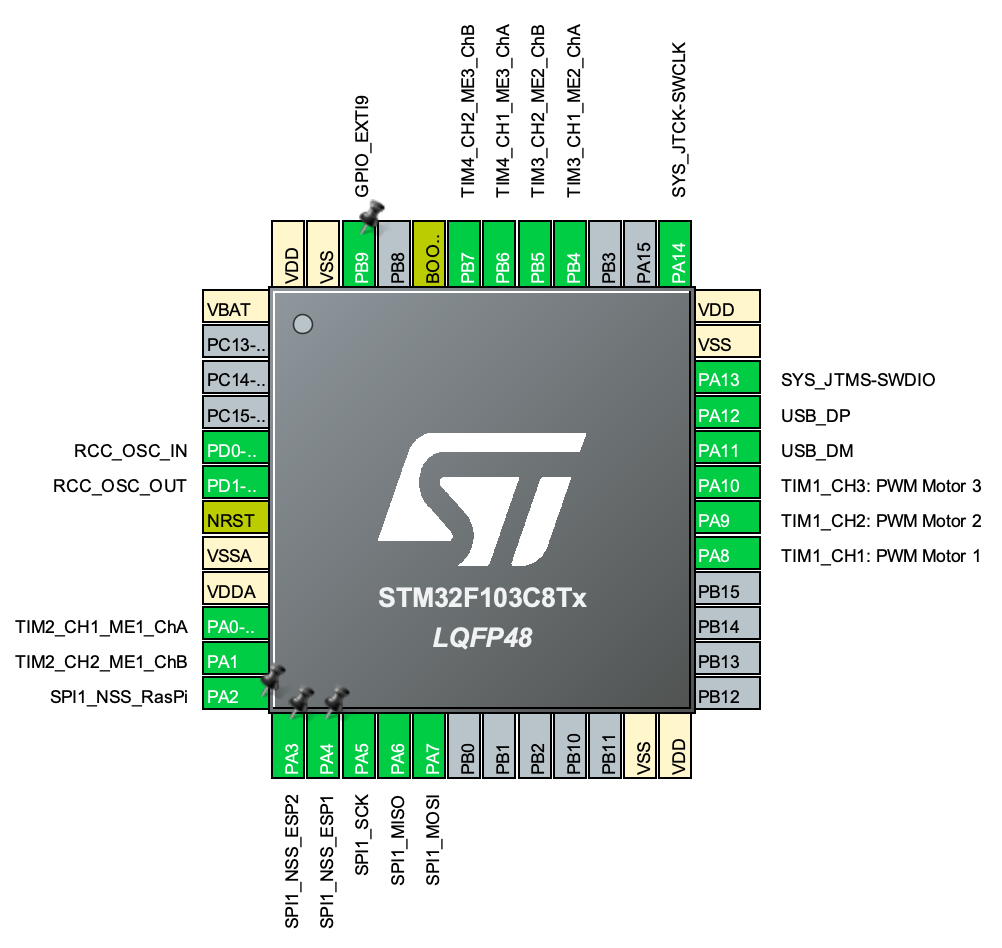
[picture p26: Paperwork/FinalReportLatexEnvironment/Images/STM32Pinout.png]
          \\
          \caption{ STM32F103C8T6 Pinout } 
          \label{fig:STM32Pinout}
      \end{center}
    \end{figure}

    \newpage

    \section{STM32 Code}

    \begin{figure}
      \begin{lstlisting}[language=C]
        void HAL_GPIO_EXTI_Callback(uint16_t GPIO_Pin) {
          if((GPIO_Pin == GPIO_PIN_9)) {
            if((HAL_GPIO_ReadPin(GPIOB, GPIO_PIN_9) == GPIO_PIN_SET)){
                HAL_TIM_PWM_Stop(&htim1, TIM_CHANNEL_1);
                HAL_TIM_PWM_Stop(&htim1, TIM_CHANNEL_2);
                HAL_TIM_PWM_Stop(&htim1, TIM_CHANNEL_3);
                }
          }
          else{
            __NOP();
          }
        }
        \end{lstlisting}
        \caption{Limit Switch Interrupt Functionality}
        \label{fig:interrupt}
    \end{figure}

    \begin{figure}
      \begin{lstlisting}[language=C]
        void SPIConfig (void){
          RCC->APB2ENR |= (1<<12);  // Enable SPI1 CLock
          SPI1->CR1 |= (1<<0)|(1<<1);   // CPOL=1, CPHA=1
          SPI1->CR1 |= (1<<2);  // Master Mode
          SPI1->CR1 |= (3<<3);  // BR[2:0] = 011: fPCLK/16, PCLK2 = 80MHz, SPI clk = 5MHz
          SPI1->CR1 &= ~(1<<7);  // LSBFIRST = 0, MSB first
          SPI1->CR1 |= (1<<8) | (1<<9);  // SSM=1, SSi=1 -> Software Slave Management
          SPI1->CR1 &= ~(1<<10);  // RXONLY = 0, full-duplex
          SPI1->CR1 &= ~(1<<11);  // DFF=0, 8 bit data
          SPI1->CR2 = 0;
        }
	    \end{lstlisting}
     \caption{SPI Config Setup}
     \label{fig:SPIConfig}
    \end{figure}

    \newpage

    \begin{figure}
      \begin{lstlisting}[language=C]
        void SPI_Transmit (uint8_t *data, int size){

          /************** STEPS *****************
          1. Wait for the TXE bit to set in the Status Register
          2. Write the data to the Data Register
          3. After the data has been transmitted, wait for the BSY bit to reset in Status Register
          4. Clear the Overrun flag by reading DR and SR
          ************************************************/

          int i=0;
          while (i<size){
            while (!((SPI1->SR)&(1<<1))) {};  // wait for TXE bit to set -> This will indicate that the buffer is empty
            SPI1->DR = data[i];  // load the data into the Data Register
            i++;
          }

        /*During discontinuous communications, there is a 2 APB clock period delay between the
        write operation to the SPI_DR register and BSY bit setting. As a consequence it is
        mandatory to wait first until TXE is set and then until BSY is cleared after writing the last
        data.
        */
          while (!((SPI1->SR)&(1<<1))) {};  // wait for TXE bit to set -> This will indicate that the buffer is empty
          while (((SPI1->SR)&(1<<7))) {};  // wait for BSY bit to Reset -> This will indicate that SPI is not busy in communication

          //  Clear the Overrun flag by reading DR and SR
          uint8_t temp = SPI1->DR;
                  temp = SPI1->SR;
        }
      \end{lstlisting}
      \caption{SPI Transmit Setup}
      \label{fig:SPI_Transmit}
    \end{figure}

\begin{figure}
      \begin{lstlisting}[language=C]
        void SPI_Receive (uint8_t *data, int size){
          /************** STEPS *****************
          1. Wait for the BSY bit to reset in Status Register
          2. Send some Dummy data before reading the DATA
          3. Wait for the RXNE bit to Set in the status Register
          4. Read data from Data Register
          ************************************************/

          while (size){
            while (((SPI1->SR)&(1<<7))) {};  // wait for BSY bit to Reset -> This will indicate that SPI is not busy in communication
            SPI1->DR = 0;  // send dummy data
            while (!((SPI1->SR) &(1<<0))){};  // Wait for RXNE to set -> This will indicate that the Rx buffer is not empty
            *data++ = (SPI1->DR);
            size--;
          }
        }
      \end{lstlisting}
      \caption{SPI Receive Setup}
      \label{fig:SPI_Receive}
    \end{figure}

\begin{figure}
      \begin{lstlisting}[language=C]
        void GPIOConfig (void){
          RCC->APB2ENR |=  (1<<2);  // Enable GPIOA clock
          GPIOA->CRL = 0;
          GPIOA->CRL |= (11U<<20);   // PA5 (SCK) AF output Push Pull
          GPIOA->CRL |= (11U<<28);   // PA7 (MOSI) AF output Push Pull
          GPIOA->CRL |= (1<<26);    // PA6 (MISO) Input mode (floating)
          GPIOA->CRL |= (3<<16);    // PA4 used for CS, GPIO Output
        }
	    \end{lstlisting}
    \caption{SPI GPIO Chip Select Setup}
    \label{fig:GPIOConfig}
\end{figure}

\begin{figure}
      \begin{lstlisting}[language=C]
        void SPI_Enable (void){
          SPI1->CR1 |= (1<<6);   // SPE=1, Peripheral enabled
        }

        void SPI_Disable (void){
          SPI1->CR1 &= ~(1<<6);   // SPE=0, Peripheral Disabled
        }

        void CS_Enable (void){
          GPIOA->BSRR |= (1<<9)<<16;
        }

        void CS_Disable (void){
          GPIOA->BSRR |= (1<<9);
        }

        uint8_t RxData[3]; // receive SPI data bytes
        
        \end{lstlisting}
        \caption{SPI Enable and Disable Setup}
        \label{fig:SPI_Enable}
    \end{figure}

    \begin{figure}
      \begin{lstlisting}[language=C]
        // Maps PWM speed between a range
        uint32_t MAP(uint32_t au32_IN, uint32_t au32_INmin, uint32_t au32_INmax, uint32_t au32_OUTmin, uint32_t au32_OUTmax){
            return ((((au32_IN - au32_INmin)*(au32_OUTmax - au32_OUTmin))/(au32_INmax - au32_INmin)) + au32_OUTmin);
        }
        
        // Maps speed between a limit
        int mapChannel(int speed, int minLimit, int maxLimit){
          return MAP(speed, -20, 20, minLimit, maxLimit);
        }

        // PWM Timer Setup
        MX_TIM1_Init(); // Initialize all configured peripherals

        HAL_TIM_PWM_Start(&htim1, TIM_CHANNEL_1); // Setting up PWM Timer
        HAL_TIM_PWM_Start(&htim1, TIM_CHANNEL_2); // Setting up PWM Timer
        HAL_TIM_PWM_Start(&htim1, TIM_CHANNEL_3); // Setting up PWM Timer

        HAL_TIM_Encoder_Start_IT(&htim2, TIM_CHANNEL_ALL); // Setting up Encoders
        HAL_TIM_Encoder_Start_IT(&htim3, TIM_CHANNEL_ALL);
        HAL_TIM_Encoder_Start_IT(&htim4, TIM_CHANNEL_ALL);

        while(1){
          htim1.Instance->CCR1 = mapChannel(M1_Speed, 1100, 1884); // current, minimum, maximum, default
          htim1.Instance->CCR2 = mapChannel(M2_Speed, 1100, 1884);
          htim1.Instance->CCR3 = mapChannel(M3_Speed, 1100, 1884);

          HAL_Delay(3000);
        }

	    \end{lstlisting}
     \caption{PWM Setup and Motor Control}
     \label{fig:PWM}
    \end{figure}

    \appendix

    \chapter{Appendix}

    \section{Terms and Keywords}
    \begin{itemize}
        \item ChILD - Children's Interstitial and Diffuse Lung Disease
        \item PCB – Printed Circuit Board
        \item OWB - Three-Wheeled Omni-Wheel Bot
        \item UWB - Ultra-wideband is a radio technology that can use a very low energy level for short-range, high-bandwidth communications over a large portion of the radio spectrum.
        \item ESP32 - A series of low-cost, low-power system-on-a-chip microcontrollers with integrated Wi-Fi and dual-mode Bluetooth.
        \item RPM - Revolutions per minute
        \item GPIO - General-purpose input/output
        \item SPI - Serial Peripheral Interface
        \item PWM - Pulse-width modulation
        \item MPH - Miles per hour
        \item OpenCV - (Open Source Computer Vision Library) is an open source computer vision and machine learning software library.
        \item TDoA - Time Difference of Arrival 
        \item ToF - Time of Flight
        \item BOM - Bill of materials
        \item BLE - Bluetooth Low Energy
        \item LDO - Low Dropout Voltage Regulator
        \item PTC - Positive Temperature Coefficient, PTC fuses are made of a material that increases its internal resistance as the temperature increases.
    \end{itemize}

    \bibliographystyle{IEEEtran}
    \bibliography{ref}

\end{document} % This is the end of the document

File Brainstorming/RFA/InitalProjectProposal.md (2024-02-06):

# Project Details (Approved Feb. 1st 2024)
## Oxygen Delivery Robot

Team Members:
- Rutvik Sayankar (rutviks2)
- Aidan Dunican (dunican2)
- Nazar Kalyniouk (nazark2)

## Problem

Children's interstitial and diffuse lung disease (ChILD) is a collection of diseases or disorders. These diseases cause a thickening of the interstitium (the tissue that extends throughout the lungs) due to scarring, inflammation, or fluid buildup. This eventually affects a patient’s ability to breathe and distribute enough oxygen to the blood.

Numerous children experience the impact of this situation, requiring supplemental oxygen for their daily activities. It hampers the mobility and freedom of young infants, diminishing their growth and confidence. Moreover, parents face an increased burden, not only caring for their child but also having to be directly involved in managing the oxygen tank as their child moves around.

## Solution

Given the absence of relevant solutions in the current market, our project aims to ease the challenges faced by parents and provide the freedom for young children to explore their surroundings. As a proof of concept for an affordable solution, we propose a three-wheeled omnidirectional mobile robot capable of supporting filled oxygen tanks in the size range of M-2 to M-9, weighing 1 - 6kg (2.2 - 13.2 lbs) respectively (when full). Due to time constraints in the class and the objective to demonstrate the feasibility of a low-cost device, we plan to construct a robot at a ~50% scale of the proposed solution. Consequently, our robot will handle simulated weights/tanks with weights ranging from 0.5 - 3 kg (1.1 - 6.6 lbs).

The robot will have a three-wheeled omni-wheel drive train, incorporating two localization subsystems to ensure redundancy and enhance child safety. The first subsystem focuses on the drivetrain and chassis of the robot, while the second subsystem utilizes ultra-wideband (UWB) transceivers for triangulating the child's location relative to the robot in indoor environments. As for the final subsystem, we intend to use a camera connected to a Raspberry Pi and leverage OpenCV to improve directional accuracy in tracking the child.

As part of the design, we intend to create a PCB in the form of a Raspberry Pi hat, facilitating convenient access to information generated by our computer vision system. The PCB will incorporate essential components for motor control, with an STM microcontroller serving as the project's central processing unit. This microcontroller will manage the drivetrain, analyze UWB localization data, and execute corresponding actions based on the information obtained.

## Solution Components

### Subsystem 1: Drivetrain and Chassis

This subsystem encompasses the drive train for the 3 omni-wheel robot, featuring the use of 3 H-Bridges (L298N - each IC has two H-bridges therefore we plan to incorporate all the hardware such that we may switch to a 4 omni-wheel based drive train if need be) and 3 AndyMark 245 RPM 12V Gearmotors equipped with 2 Channel Encoders. The microcontroller will control the H-bridges. The 3 omni-wheel drive system facilitates zero-degree turning, simplifying the robot's design and reducing costs by minimizing the number of wheels. An omni-wheel is characterized by outer rollers that spin freely about axes in the plane of the wheel, enabling sideways sliding while the wheel propels forward or backward without slip. Alongside the drivetrain, the chassis will incorporate 3 HC-SR04 Ultrasonic sensors (or three bumper-style limit switches - like a Roomba), providing a redundant system to detect potential obstacles in the robot's path.

### Subsystem 2: UWB Localization
This subsystem suggests implementing a module based on the DW1000 Ultra-Wideband (UWB) transceiver IC, similar to the technology found in Apple AirTags. We opt for UWB over Bluetooth due to its significantly superior accuracy, attributed to UWB's precise distance-based approach using time-of-flight (ToF) rather than meer signal strength as in Bluetooth.

This project will require three transceiver ICs, with two acting as "anchors" fixed on the robot. The distance to the third transceiver (referred to as the "tag") will always be calculated relative to the anchors. With the transceivers we are currently considering, at full transmit power, they have to be at least 18" apart to report the range. At minimum power, they work when they are at least 10 inches. For the "tag," we plan to create a compact PCB containing the transceiver, a small coin battery, and other essential components to ensure proper transceiver operation. This device can be attached to a child's shirt using Velcro.

### Subsystem 3: Computer Vision
This subsystem involves using the OpenCV library on a Raspberry Pi equipped with a camera. By employing pre-trained models, we aim to enhance the reliability and directional accuracy of tracking a young child. The plan is to perform all camera-related processing on the Raspberry Pi and subsequently translate the information into a directional command for the robot if necessary. Given that most common STM chips feature I2C buses, we plan to communicate between the Raspberry Pi and our microcontroller through this bus.

### Division of Work:
Given that we already have a 3 omni wheel robot, it is a little bit smaller than our 50% scale but it allows us to immediately begin work on UWB localization and computer vision until a new iteration can be made. Simultaneously, we'll reconfigure the drive train to ensure compatibility with the additional systems we plan to implement, and the ability to move the desired weight. To streamline the process, we'll allocate specific tasks to individual group members – one focusing on UWB, another on Computer Vision, and the third on the drivetrain. This division of work will allow parallel progress on the different aspects of the project.

## Criterion For Success

1. Omni-wheel drivetrain that can drive in a specified direction that is defined by UWB system.
2. UWB Localization down to an accuracy of < 1m.
3. Close-range object detection system that can detect objects inside the path of travel and alert the user.

** define power levels on block diagram

### Initial considerations

We are currently in discussion with Greg at the machine shop about switching to a four-wheeled omni-wheel drivetrain due to the increased weight capacity and integrity of the chassis. To address the safety concerns of this particular project, we are planning to implement the following safety measures:
- Limit robot max speed to <5 MPH
- Using Empty Tanks/ simulated weights. At NO point ever will we be working with compressed oxygen. Our goal is just to prove that we can build a robot that can follow a small human.
- We are planning to work extensively to design the base of the robot to be bottom-heavy & wide to prevent the tipping hazard.

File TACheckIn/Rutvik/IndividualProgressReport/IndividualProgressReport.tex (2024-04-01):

\documentclass{report}

\usepackage{amsmath}
\usepackage{graphicx} % to insert images
\graphicspath{{../pdf/}{/Users/rutviksayankar/Repos/ECE445_SP24/TACheckIn/Rutvik/IndividualProgressReport/Images}} % setting up path for image storage
\usepackage{hyperref} % allows table of contents to be clickable to sections
\hypersetup{
    colorlinks,
    citecolor=blue,
    filecolor=blue,
    linkcolor=blue,
    urlcolor=blue
}

\title{ECE 445: Senior Design Lab \\ Individual Progress Report} % Sets article title
\author{Rutvik Sayankar} % Sets authors name
\date{\today} % Sets date for date compiled

% The preamble ends with the command \begin{document}
\begin{document}
    \maketitle % creates title using information in preamble (title, author, date)
    
    \pagebreak
    \tableofcontents % creates table of contents
    \pagebreak

    \section{Terms and Keywords}
    \vspace{0.8cm}
    \begin{itemize}
        \item ChILD - Children's Interstitial and Diffuse Lung Disease
        \item PCB – Printed Circuit Board
        \item OWB - Three-Wheeled Omni-Wheel Bot
        \item UWB - Ultra-wideband is a radio technology that can use a very low energy level for short-range, high-bandwidth communications over a large portion of the radio spectrum.
        \item ESP32 - A series of low-cost, low-power system-on-a-chip microcontrollers with integrated Wi-Fi and dual-mode Bluetooth.
        \item RPM - Revolutions per minute
        \item GPIO - General-purpose input/output
        \item SPI - Serial Peripheral Interface
        \item PWM - Pulse-width modulation
        \item MPH - Miles per hour
        \item OpenCV - (Open Source Computer Vision Library) is an open source computer vision and machine learning software library.
        \item OpenPose - Real-time multi-person keypoint detection library for body, face, hands, and foot estimation.
        \item TDoA - Time Difference of Arrival 
        \item ToF - Time of Flight
    \end{itemize}

    \pagebreak

    \chapter{Introduction}
    \section{Team Project Overview}
    Children's interstitial and diffuse lung disease (ChILD) is a collection of diseases or disorders. These diseases cause a thickening of the interstitium (the tissue that extends throughout the lungs) due to scarring, inflammation, or fluid buildup \cite{ChILD-2022}. This eventually affects a patient’s ability to breathe and distribute enough oxygen to the blood. Numerous children experience the impact of this situation, requiring supplemental oxygen for their daily activities. It hampers the mobility and freedom of young infants, diminishing their growth and confidence. Moreover, parents face an increased burden, not only caring for their child but also having to be directly involved in managing the oxygen tank as their child moves around.

    Given the absence of relevant solutions in the current market, our project aims to ease the challenges faced by parents and provide the freedom for young children to explore their surroundings. As a proof of concept for an affordable solution, we propose a three-wheeled omnidirectional mobile robot capable of supporting a filled M-6 oxygen tank. We plan to implement two localization subsystems to ensure redundancy and enhance child safety. The first subsystem utilizes ultra-wide band (UWB) transceivers for triangulating the child's location relative to the robot in indoor environments, this is similar to how Apple AirTags triangulate their location relative to an iPhone \cite{airtag_uwb} (although AirTags use a combination of UWB and Bluetooth triangulation \cite{airtag_ble}). The second subsystem makes use of a desktop web camera which streams video to a Raspberry Pi where it will leverage open-source object tracking libraries to improve our directional accuracy in tracking a child. The final main subsystem focuses on the drive train, chassis and close range object detection of the robot.

    \section{Individual Responsibilities}
    My individual responsibilities are as follows:

    \begin{itemize}
        \item Overall project management
        \item Research, design and implementation of OWB triangulation system
        \item Design and Routing of PCB
        \item Aid in PCB assembly and testing
        \item Aid in chassis design
        \item Aid in bumper limit switch design
        \item Handle all 3D printing
        \item Handling parts ordering for parts that use money outside of provided budget
    \end{itemize}

    \chapter{Individual Design Work}
    \section{Design Considerations \& Diagrams}

    \subsection{PCB Design}
    The design of the schematic of the PCB was done due to the main required components and what all was needed to ensure the components were properly powered and able to communicate, I completed all of the parts except for the power regulation circuits. The layout of the PCB required a different style of thought (\ref{fig:MainBoardv1.1_Layout}). I had to consider how the board would be used, what connections would come out of the board and in what direction they would need to face. This is important as it would help prevent wiring from getting messy and therefore preventing any possible issues that may arrise from having messy wiring. I chose to keep the motor power, PWM and encoder wiring close together on the layout. Each of those things are also facing the same direction, this should help ensure that wiring won't get tangled together. The connections for the SPI bus are all also facing the same direction. Finally, the power input from the battery is far away from other connections, and should not get mixed up with anything else on the board.

    Knowing the importance of visual indicators during debugging, I have added LEDs for each power level to help indicate when the circuit is live and when power has been properly stepped down. Aside from general PCB organization, a very helpful item that has been added is the QR code linking to our project Github that is on the board. This gives us the ability to quickly check for something incase any issue arrises and it gives a third party observer a place to learn more about the project.

    Finally, understanding the importance of knowing the connections during debugging I've ensured that I have labeled as much as possible in terms of connectors and pins. There should be no confusion when wiring or PCB assembly in terms of what goes where.

    \begin{figure}[ht!]
        \centering
        
        \caption{MainBoardv1.1 Main Schematic}
        \label{fig:MainSchematic}
    \end{figure}

    \begin{figure}[ht!]
        \centering
        
        \caption{MainBoardv1.1 Power Schematic}
        \label{fig:PowerSchematic}
    \end{figure}

    \begin{figure}[ht!]
        \centering
        
        \caption{MainBoardv1.1 OR3 Gate Schematic}
        \label{fig:ORSchematic}
    \end{figure}

    \begin{figure}[ht!]
        \centering
        
        \caption{MainBoardv1.1 Board Layout}
        \label{fig:MainBoardv1.1_Layout}
    \end{figure}
    
    \subsection{UWB System}
    After ordering the UWB transceivers from \href{https://www.makerfabs.com/esp32-uwb-dw3000.html}{MakerFabs} I was able to get started on testing out the accuracy of the transceivers, and seeing how I would be able to send packets back and forth. I began by implementing a simple ranging test (\ref{fig:UWBRanging}). With some moving around of the transceivers I was able to get a fairly accurate reading of the distance between two transceivers (\ref{fig:UWBRangingSerialMonitor}).

    I am currently in progress tweaking the triangulation code with three transceivers, to get a location relative to two anchors.

    \begin{figure}[ht!]
        \centering
        
        \caption{UWB Ranging Test}
        \label{fig:UWBRanging}
    \end{figure}

    \begin{figure}[ht!]
        \centering
        
        \caption{UWB Ranging Test - Serial Monitor Output}
        \label{fig:UWBRangingSerialMonitor}
    \end{figure}

    \subsection{Bumper Limit Switch \& 3D Printing}

    I have worked with Aidan on desiging the bumper limit switch. Mainly I have been focused on the 3D printablity of the part. Testing the prints, and seeing what tweaks need to be made. Currently we're focusing on modularity of the bumper. Creating a screw connector between the actual bumper and the limit switch (\ref{fig:LimitSwitchScrewTerminal}). This way if something gets damaged on impact we only have to reprint one part of the assembly.

    \begin{figure}[ht!]
        \centering
        
        \caption{Test Prints for the Limit Switch Screw Terminal}
        \label{fig:LimitSwitchScrewTerminal}
    \end{figure}

    \subsection{Chassis Design \& Build}
    I have been in close talks with the ECE Machine Shop specifically Gregg and Jordan regarding the design and manufacturing of the robot. We been able to sort out many issues and design questions, the main questions being the following:

    \begin{itemize}
        \item Q: How to mount the omni-wheel onto the short motor axle?
        \item A: Custom axle to wheel hub should be built.
        \item Q: How to position the oxygen tank to lower the center of gravity to maintain robot stability and safety?
        \item A: We will be cutting a hole in the top level and lowering the oxygen tank to rest on the bottom level and be supported laterally by the top level (NOT shown in figure \ref{fig:RobotChassisBuild}).
        \item Q: Robot base material, what is best to ensure a low center of gravity?
        \item A: Medium-density fiberboard (MDF) is a great option and if needed we can add extra weight to the underside of the robot chassis.
        \item Q: How to support robot weight, is something extra like a caster wheel required under the center of the robot?
        \item A: MDF will be sturdy enought given our weight requirements.
    \end{itemize}

    The inital CAD design of the robot I designed can be seen in figure \ref{fig:Robot_CAD}. The current version of the robot chassis can be seen in figure \ref{fig:RobotChassisBuild}.

    \begin{figure}[ht!]
        \centering
        
        \caption{Inital Robot CAD Assembly}
        \label{fig:Robot_CAD}
    \end{figure}

    \begin{figure}[ht!]
        \centering
        
        \caption{Current Robot Chassis Assembly}
        \label{fig:RobotChassisBuild}
    \end{figure}

    \section{Testing/Verification}
    \label{sec:Testing}
    In terms of testing we will be using a modular testing plan, testing various subsystems individually. The week of March 25th is currently being used for testing of the accuracy for UWB triangulation. If testing passes then we can begin implementing the direction vector calculations that will help give the robot a direction to follow from the UWB data. Following that, testing of the power systems on the V1.1 of the PCB is also happening this week (our current bottleneck if the arrival of the PCBs), but we have all the components required, any issues will get revised and sent out in the fourth round of PCB orders. The hole in the top level of the chassis was completed on \today, and the robot motor and movement testing will occur during the week of April 1st. These are the main systems that require testing. Unfortunately, no further data has been gathered to show results in the form of graphs or tables but will be created within the next two weeks.

    \subsection{Contingency plans for failed tests}
    If testing fails on the UWB subsystem and we are unable to get the system to accurately triangulation location, we will be able to use the UWB for ranging which is already functional. With this and an angular vector provided from the Computer Vision subsystem we will still be able to accurately track a child.

    If testing fails on the power subsystem of the PCB, we have a Power Distribution Panel from an old FRC robot that can easily be used to help supply the power to the motors and we will breadboard our 5V supply power.

    \chapter{Conclusion}

    \section{Self-assessment}
    I do believe I have a slightly heavy workload for this project, but it is something I am aware of and okay with given the number of tasks required to complete this project. Following that, I believe we are slightly behind schedule. There are many unknowns we need to account for and need to give ourselves as much time as possible to sort them out.

    \section{Plans for remaining work}
    Please refer to the section \ref{sec:Testing} for the the short term plan. After that point it will be subsystem integration, where we will performing sensor fusions of the UWB and computer vision subsystem, and integrating the rest of the subsystems onto the chassis. I believe we are on track to finish the project, but it will definitely require all hands on deck to get it done properly.

    \section{Ethics and Safety}
    \subsection{Ethical Considerations}
    As we continue through the development of our project, we are unwavering in our dedication to abide by the ethical and safety principles outlined by the Association for Computing Machinery (ACM) and the Institute of Electrical and Electronics Engineers (IEEE). As we embark on this project, we pledge our commitment to adhere to these standards, ensuring that our actions and choices uphold the highest level of professionalism and integrity.

    As outlined in Section I of the IEEE Code of Ethics, we pledge to “uphold the highest standards of integrity, responsible behavior, and ethical conduct in professional activities” \cite{IEEE_2020}. We will prioritize safety in our design and adhere to ethical design practices. Educating the parents and caregivers about the robot’s use and limitations will allow for informed decision-making. Following relevant laws and regulations regarding this technology will also be a high priority.

    In the same Code of Ethics, outlined in Section III, we pledge to “strive to ensure this code is upheld by colleagues and co-workers” \cite{IEEE_2020}. We will support each other in ethical conduct and foster a culture of ethical behavior. Open communication will be established and encouraged to raise concerns and provide guidance to team members.

    \subsection{Safety Considerations}
    This project aligns with the safety principles outlined in the ACM Code of Ethics and Professional Conduct. Safety remains our number one priority and as outlined in Section 1.2 \cite{ACM_2018}, we will avoid negative consequences, especially when those consequences are significant and unjust. We will take careful consideration of potential impacts and minimize harm. In the context of this project, we will ensure that the robot’s design and operation prioritizes safety, especially to the children this product aims to assist. We will work to analyze potential risk and consider the robot’s mobility and interaction with its environment.

    As well as promoting safety, privacy is also a very important guideline that will be followed, which is outlined in Section 1.6. As professionals, we must safeguard the personal information of our users, especially if it involves children. As it relates to this project, we will ensure that no data will be collected and stored in an external location. Data collection will be minimized to only what is necessary for the robot to operate.

    One aspect of our project where safety must be considered is regarding the use of lithium batteries. We acknowledge the potential risks associated with the misuse of lithium batteries. We are committed to following the safety guidelines associated with the batteries we plan on using. More specifically, maintaining the battery’s temperature within the recommended range. Also, we are dedicated to the responsible disposal of batteries to ensure sustainability.

    Since we are incorporating motors into our design, we will deploy essential control systems to mitigate potential hazards such as collisions with the environment. Safe operation will be ensured with the use of sensors, vision systems, and warning systems.

    \bibliographystyle{IEEEtran}
    \bibliography{ref}

\end{document} % This is the end of the document

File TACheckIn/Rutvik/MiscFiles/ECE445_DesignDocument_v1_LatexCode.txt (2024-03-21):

\documentclass[journal,onecolumn, draftclsnofoot, 12pt]{IEEEtran}
\usepackage[margin=1in]{geometry}
\usepackage[utf8]{inputenc}
\usepackage{graphicx}
\usepackage{times}
\usepackage{algorithm}
\usepackage{algpseudocode}
\usepackage{graphicx}
\usepackage{amsmath}
\usepackage{subcaption}
\usepackage{amsmath,amsfonts,amssymb,amsthm,commath,dsfont,enumitem}
\usepackage[colorlinks,urlcolor=blue,citecolor=blue]{hyperref}
\usepackage{xcolor}
\usepackage{listings}
\usepackage{todonotes}
\usepackage[T1]{fontenc}
\usepackage{graphicx} % for including the logo
\usepackage{fancyhdr} % for customizing the footer
\usepackage{tikz} % for the flowchart
\usetikzlibrary{shapes.geometric} % for tikz charts
\usetikzlibrary {arrows.meta,bending,positioning} % for tikz charts
\usepackage{array} % for R&V Tables
\usepackage{hyperref} % for hyper links

\pagestyle{fancy}

% % Define a new command to include a logo
% \newcommand{\logo}{\includegraphics[width=1.0cm]{OWB_cutout.png}}

% % Customize the footer to include the logo on the bottom right of pages 3 to 5
% \fancyfoot[LO,RE]{\ifnum\value{page}>3\ifnum\value{page}<19\logo\fi\fi}

% Setting color formatting for Python code
\lstset{
    language=Python,
    basicstyle=\fontsize{8}{10}\ttfamily,
    keywordstyle=\color{blue},
    stringstyle=\color{red},
    commentstyle=\color{green},
    morecomment=[l][\color{magenta}]{\#},
}

% Setting color formatting for C code
\lstset{
    language=C,
    basicstyle=\fontsize{8}{10}\ttfamily,
    keywordstyle=\color{blue},
    stringstyle=\color{red},
    commentstyle=\color{green!50!black},
    morecomment=[l][\color{magenta}]{\#},
    frame=tb,
    numbers=left,
    numberstyle=\tiny\color{gray},
    breaklines=true,
    showstringspaces=false,
}

% macros adapted from matus & djhsu
\def\ddefloop#1{\ifx\ddefloop#1\else\ddef{#1}\expandafter\ddefloop\fi}
\def\ddef#1{\expandafter\def\csname bb#1\endcsname{\ensuremath{\mathbb{#1}}}}
\ddefloop ABCDEFGHIJKLMNOPQRSTUVWXYZ\ddefloop
\def\ddef#1{\expandafter\def\csname b#1\endcsname{\ensuremath{\mathbf{#1}}}}
\ddefloop ABCDEFGHIJKLMNOPQRSTUVWXYZ\ddefloop
\def\ddef#1{\expandafter\def\csname c#1\endcsname{\ensuremath{\mathcal{#1}}}}
\ddefloop ABCDEFGHIJKLMNOPQRSTUVWXYZ\ddefloop

\DeclareMathOperator*{\argmin}{arg\,min}
\DeclareMathOperator*{\argmax}{arg\,max}
\DeclareMathOperator*{\softmax}{softmax}

\newenvironment{Q}{\item}{\phantom{s}}
\newenvironment{Solution}{\color{blue}\begin{enumerate}}{\end{enumerate}}

\begin{document}
\maketitle

\begin{titlepage}
    \begin{center}
        \vspace*{1cm}
            
        \Huge
        \textbf{ECE 445 Design Document - Spring 2024}
            
        \vspace{0.5cm}
        \LARGE
        OXYGEN DELIVERY ROBOT
            
        \vspace{1.5cm}

        \large
        Team \#27 \\
        Rutvik Sayankar \\ Aidan Dunican \\ Nazar Kalyniouk \\

        \vspace{1cm}
        
        TA: Selva Subramaniam

        \vspace{1.5cm}
            
        \vfill

        \vspace{0.8cm}
            
        \Large
        February 22nd, 2024 \\
        ECE 445: Senior Design Project Lab \\
        University of Illinois at Urbana-Champaign\\
            
    \end{center}
\end{titlepage}

\pagebreak

\tableofcontents

\pagebreak

\section{Terms and Keywords}
\vspace{0.8cm}
\begin{itemize}
    \item ChILD - Children's Interstitial and Diffuse Lung Disease
    \item PCB – Printed Circuit Board
    \item OWB - Three-Wheeled Omni-Wheel Bot
    \item UWB - Ultra-wideband is a radio technology that can use a very low energy level for short-range, high-bandwidth communications over a large portion of the radio spectrum.
    \item ESP32 - A series of low-cost, low-power system-on-a-chip microcontrollers with integrated Wi-Fi and dual-mode Bluetooth.
    \item RPM - Revolutions per minute
    \item GPIO - General-purpose input/output
    \item PWM - Pulse-width modulation
    \item MPH - Miles per hour
    \item OpenCV - (Open Source Computer Vision Library) is an open source computer vision and machine learning software library.
    \item OpenPose - Real-time multi-person keypoint detection library for body, face, hands, and foot estimation.
    \item TDoA - Time Difference of Arrival 
    \item ToF - Time of Flight
\end{itemize}

\pagebreak

\section{Introduction}

\subsection{Problem}
Children's interstitial and diffuse lung disease (ChILD) is a collection of diseases or disorders. These diseases cause a thickening of the interstitium (the tissue that extends throughout the lungs) due to scarring, inflammation, or fluid buildup \cite{ChILD-2022}. This eventually affects a patient’s ability to breathe and distribute enough oxygen to the blood.

Numerous children experience the impact of this situation, requiring supplemental oxygen for their daily activities. It hampers the mobility and freedom of young infants, diminishing their growth and confidence. Moreover, parents face an increased burden, not only caring for their child but also having to be directly involved in managing the oxygen tank as their child moves around.

\subsection{Solution}
Given the absence of relevant solutions in the current market, our project aims to ease the challenges faced by parents and provide the freedom for young children to explore their surroundings. As a proof of concept for an affordable solution, we propose a three-wheeled omnidirectional mobile robot capable of supporting filled oxygen tanks in the size range of M-2 to M-9, weighing 2.2 - 13.2 lbs (1 - 6kg) respectively (when full). Due to time constraints in the class and the objective to demonstrate the feasibility of a low-cost device, we plan to construct the robot at a roughly 50 percent scale of the proposed solution. Consequently, our robot will handle simulated weights/tanks with weights ranging from 1.1 - 6.6 lbs (0.5 - 3 kg). For our prototyping and testing, we will be utilizing an empty M-6 oxygen tank (height = 15", diameter = 3.2", empty weight = 2.8 lbs/1.27kg, capacity = 165L \cite{oxygen_tank_sizes}).

As mentioned the robot will have a three-wheeled omni-wheel drive train, incorporating two localization subsystems to ensure redundancy and enhance child safety. The first subsystem utilizes ultra-wide band (UWB) transceivers for triangulating the child's location relative to the robot in indoor environments, this is similar to how Apple AirTags triangulate their location relative to an iPhone \cite{airtag_uwb} (although AirTags use a combination of UWB and Bluetooth triangulation \cite{airtag_ble}). The second subsystem makes use of a desktop web camera which streams video to a Raspberry Pi where it will leverage open-source object tracking libraries to improve our directional accuracy in tracking a child. The final main subsystem focuses on the drive train and chassis of the robot.

As part of the design, we intend to create a PCB in the form of a Raspberry Pi hat, facilitating convenient access to information generated by our computer vision system, and saving space on our robot. The PCB will incorporate all motor control components, limit switch connections, GPIO pass through for the Raspberry Pi, power distribution and step down converter, and an STM32 based microcontroller serving as the project's central processing unit. This microcontroller will control the drivetrain, analyze UWB localization data, and use the direction vector provided by the computer vision system to calculate the speed and direction of each wheel.

\subsection{Visual Aid}

\begin{figure}[H]
\begin{center}
\includegraphics[width=0.9\textwidth]{VisualAid.png}\\
\caption{ Visual aid for our project.  } 
\label{fig:visualaid}
\end{center}
\end{figure}

\newpage

\subsection{High-Level Requirements List}
\begin{itemize}
    \item \textbf{Omni-wheel Drivetrain}: 
    The primary requisite pertains to the ability of the omni-wheel drivetrain to maintain heading according to a directional vector provided by our localization subsystems (UWB \& Computer Vision). This system will receive a the direction vector in the form of an array with broken down direction and speeds for each motor. Consequently, upon determination of a directional vector by our software, our robot is expected to initiate movement in the designated direction within 500 milliseconds.

    \item \textbf{UWB Localization}: 
    The subsequent criterion concerns the ability of the UWB localization system to produce precise positional data, with an accuracy threshold within 1 meter. We aim for continuous real-time updates regarding the child's whereabouts in relation to the robot.
    
    \item \textbf{Close-range Object Detection}: 
    The third requirement entails the implementation of close-range object detection mechanisms to discern obstacles obstructing the robot's trajectory. It is expected to promptly notify users of impending collisions, thereby safeguarding the child's well-being and facilitating timely intervention for obstacle removal.
    
\end{itemize}

\newpage

\section{Design}
\subsection{Block Diagrams}

\begin{figure}[H]
\begin{center}
\includegraphics[width=1.0\textwidth]{BlockDiagram.png}\\
\caption{High-level block diagram for our project.  } 
\label{fig:blockdiagram}
\end{center}
\end{figure}

\subsection{Subsystems Overview}
\begin{itemize}
    \item \textbf{Drivetrain Subsystem}: The Drivetrain subsystem will encompass the motors, omni-wheels, encoder, and electronic speed controllers. It will receive instructions from the Control subsystem to control the motors and feed encoder data for drift compensation back to the Control subsystem (three-wheeled omni-wheel bots are easily affected by drift if it is not compensated for).
    \item \textbf{UWB Subsystem}: This subsystem contains tag and anchor components. The UWB tag will consist of the UWB transceiver, battery, ESP32, and onboard power distribution system. It will attach to the child that is being tracked (through velcro or some similar method). The UWB signals emitted are received by the UWB anchors. It will work with the UWB anchors subsystem to determine the location of the tag relative to the robot. The UWB anchors will consist of the UWB transceivers and ESP32s. This subsystem communicates with the Control Subsystem to relay a distance and angle that corresponds to the position of the tag relative to the anchors. Both of these systems will utilize transceiver boards based on Decawave DW3000 ICs \cite{9881375}.
    \item \textbf{Computer Vision Subsystem}: This subsystem will include a web camera connected to a Raspberry Pi. Implementing an image-processing algorithm using OpenCV or OpenPose it will analyze data from the web camera to locate the child. It will connect to the microprocessor and provide an angle. This angle will correspond to the change in angle required by the robot to keep the child within the center of the image frame (this will correspond to directly in front of the robot).
    \item \textbf{Close-Range Object Detection System}: This subsystem, consisting of bumper-style limit switches will communicate with the Control Subsystem to provide information about nearby obstacles. When an obstacle is detected (i.e. a limit switch has been activated), the user will be alerted to adjust the robot's path or clear the obstacle (through an LED or simple speaker). This feature will ensure effective obstacle avoidance and will enhance the safety of the robot.
    \item \textbf{Control and Power Subsystem}: The Control Subsystem will be responsible for taking in the distance and angle from the UWB Subsystem and the angle from the Computer Vision Subsystem. Facilitating a sensor fusion with this data, it will compute a velocity vector that the robot must move to remain within $\sim 1$ meter of the child. Using the kinematics detailed in section \ref{sec:OWBKinematics}, the velocity vector will be decomposed into its components to obtain the motor speed and direction for each omnidirectional wheel. 
    
    The Power Subsystem is responsible for supplying power to all other components of the robot. It will include a 12V battery and power distribution system. This subsystem will supply 12V power to the drive system. It will supply 5V to our STM32-based microcontroller, computer vision subsystem, and motor encoders. Lastly, it will supply 3.3V to the close-range object detection system and the UWB anchors.
\end{itemize}

\newpage

\subsection{Physical Design}
A rough idea of how everything will be put onto our robot is shown in figure \ref{fig:PhysicalDesign}.

\begin{figure}[H]
\begin{center}
    \includegraphics[width=0.8\textwidth]{PhysicalDesign.png}\\
    \caption{ Physical Layout  } 
    \label{fig:PhysicalDesign}
\end{center}
\end{figure}

\subsection{Drivetrain Subsystem}
This subsystem encapsulates everything required to move the chassis of the robot. To facilitate testing we will be using a RC Transmitter Controller which is detailed in section \ref{sec:RCController}. For more information regarding our choices of the commercial components that make up the Drivetrain Subsystem, please refer to section \ref{sec:cost}. Regarding the safety of our OWB, the Drivetrain Subsystem must accept commands from the Control Subsystem to set the relative speed of the motors.

\subsubsection{Kinematics of the OWB}
\label{sec:OWBKinematics}
In a three-wheeled omni-wheel robot, the three wheels are arranged in a triangular pattern, with one wheel at the front and two wheels at the back. Each wheel has several small omnidirectional wheels arranged in a circular pattern, which allows the robot to move in any direction.

To move the robot, each wheel is driven independently using a motor. By varying the speed and direction of each wheel, the robot can move in any direction and rotate around its center point.

The kinematics of a three-wheeled omni-wheel robot can be modeled mathematically through the below equations \cite{riky2021omnidirectional} which relate the robot's linear and angular velocities to the speed and direction of each wheel.

We first define for each wheel a direction of rotation $V_i$, and the resulting movement effected in the x and y axes, $V_ix$ and $V_iy$ as shown below.

\begin{figure}[H]
  \centering
  \begin{minipage}[b]{0.45\linewidth}
    \centering
    \includegraphics[width=\linewidth]{wheel_vector.png}
    \caption{Vector Definitions}
    \label{fig:vecdef}
  \end{minipage}
  \hfill
  \begin{minipage}[b]{0.45\linewidth}
    \centering
    \includegraphics[width=\linewidth]{OWB_vectors.PNG}
    \caption{OWB drive vectors \cite{wada2015OWB}}
    \label{fig:owb_vec}
  \end{minipage}

  \label{fig:vecs}
\end{figure}

Knowing the angle of each wheel from the vertical axis, we can compute the x and y components created by the rotation of each wheel. By summing these components together, we can get the effective motion of the robot in the x, y and yaw axes.

\[
\begin{pmatrix}
V_x \\
V_y \\
\omega
\end{pmatrix}
=
\begin{pmatrix}
1 & - \frac{1}{2} & -\frac{1}{2} \\
0 & -\frac{\sqrt{3}}{2} & \frac{\sqrt{3}}{2} \\
1 & 1 & 1
\end{pmatrix}
\begin{pmatrix}
V_1 \\
V_2 \\
V_3
\end{pmatrix}
\]
    
$V_{x}$ and $V_{y}$ are the desired linear velocities in the x and y directions, respectively, and omega is the desired angular velocity. $V_{1}$, $V_{2}$, and $V_{3}$ are the velocities of the three wheels, and L is the distance between the robot's center of mass and the wheel axes.

\[
\begin{pmatrix}
V_1 \\
V_2 \\
V_3
\end{pmatrix}
=
\begin{pmatrix}
1 & - \frac{1}{2} & -\frac{1}{2} \\
0 & -\frac{\sqrt{3}}{2} & \frac{\sqrt{3}}{2} \\
1 & 1 & 1
\end{pmatrix}^{-1}
\begin{pmatrix}
V_x \\
V_y \\
\omega
\end{pmatrix}
\]

By taking the inverse of our 3x3 component coefficient matrix above, we can solve for our individual motor speeds $V_1$, $V_2$ and $V_3$, given the desired motion in terms of $V_x$, $V_y$, and $w$.

\subsubsection{Communication for RC Controller}
\label{sec:RCController}
For our RC controller, we plan to use a Flysky FS-i6 6CH 2.4GHz Radio System RC Transmitter Controller with FS-iA6 Receiver. 

This controller communicates with its receiver, the FS-iA6, using a 2.4 GHz digital frequency-hopping spread spectrum (FHSS) communication protocol.

In FHSS, the transmitter and receiver periodically hop between different channels within the 2.4 GHz frequency band to avoid interference from other devices operating on the same frequency band. The specific channels used are selected automatically by the transmitter and receiver and can be different for each transmission.

The FS-i6 transmitter sends digital signals to the FS-iA6 receiver, which is connected to the RC vehicle's onboard electronics. The transmitter and receiver are bound together before use, which pairs them and allows them to communicate securely.

The FS-i6 transmitter has six channels of control, which means it can transmit six different control signals to the receiver at the same time. These channels can be used to control the movement of the RC vehicle's motors and servos, as well as to operate other electronic components such as lights or sound systems.

For our operations, we plan to use three channels, using our OWB as our frame of reference, we used one channel for linear control in the $x-axis$ a second for linear control in the $y-axis$, and a third channel for rotational control $w$

The OWB can move forward and backward like a normal RC car. This motion is represented by $V_y$, and is mapped to CH1 on the transmitter (refer to figure \ref{fig:ChannelDistribution} for detail on channel mapping). While a normal RC car needs a $V_y$ component to turn left or right, the OWB can "yaw" on the spot. This is represented by $w$, and is mapped to CH3 on the transmitter. The final unique motion the OWB can execute is a "drift" toward the left or right. This motion is represented by $V_x$ and is mapped to CH2 on the transmitter.

Thus, using these three channels, we can define the robot's desired $V_x$, $V_y$, and $w$. These desired motion vectors are then fed to our inverse kinematics algorithm, which breaks down our desired motion into an individual wheel speed and direction for each motor.

\begin{figure}[H]
\begin{center}
    \includegraphics[width=0.8\textwidth]{channel.png}\\
    \caption{ Channel Distribution  } 
    \label{fig:ChannelDistribution}
\end{center}
\end{figure}

\newpage

\subsubsection{Requirements and Verification}
\begin{center}
\begin{tabular}{ | m{20em} || m{20em} | } 
  \hline
  Requirements & Verification  \\ 
  \hline
  \hline
  The electronic speed controllers power the motors at the command of the board control subsystem. The commands may be to set duty cycle, set current, or set RPM. 
  & 
  Ensure the OWB is at an idle state such that the wheels are not spinning. Then, send a command to both ESCs from the board microcontroller to either set a nonzero duty cycle, current, or RPM. Confirm that both motors begin spinning.
  \\ 
  \hline
  The drivetrain must be able to maintain a speed of at least 3 MPH (that fastest speed we are comfortable following a user), with a fully loaded oxygen tank (Full tank at 3.458 lbs + roughly 10 lbs of chassis, electronics, battery weight).
  & 
  Ensure the OWB is at an idle state such that the wheels are not spinning. Load the oxygen tank onto the robot and add any extra weight to help simulate a full oxygen tank. 
  
  Set up a specific distance for the robot to drive. Using a stopwatch, time the robot as it travels the specified distance.
  
  Using an external RC controller drive the robot forward until it passes the specified distance.
  
  Using the time measurement and the specified distance, measure the speed and ensure it is > 3 MPH.
  \\
  \hline
\end{tabular}
\end{center}

\vspace{0.8cm}

\subsection{UWB Subsystem}
This subsystem encapsulates everything required to obtain a direction and angle of the UWB Tag relative to the UWB Anchors. It will transmit these values to the Control Subsystem. To facilitate the testing of our localization algorithm we will use the indoor positioning visualization example provided by MakerFabs (\url{https://github.com/Makerfabs/Makerfabs-ESP32-UWB.git}). There are two steps to our localization algorithm that are detailed in section \ref{sec:Localization}. For more information regarding our choices of the commercial components that make up the UWB Subsystem, please refer to section \ref{sec:cost}.

\vspace{0.5cm}

\subsubsection{Localization Algorithms}
\label{sec:Localization}

There are two main localization techniques when we use UWB, Time Difference of Arrival (TDoA) and Time of Flight (ToF) \cite{localization}.

ToF is a positioning method based on two-way ranging. That means the tag needs to send and receive signals from the anchor several times and then the flight time of the signal between the anchor and the tag can be measured, because radio waves travel at the speed of light, we can calculate the distance between the tag and each anchor.

TDoA is localization based on comparing the time difference between signals and each anchor and this technique requires an accurate time synchronization function. When using the TDoA method, the UWB tag will send out a poll message, and all the nearby UWB anchors will receive it and record the arrival time. Because the location of anchors is different, they won’t receive the message at the same time. We can use these time differences to determine the tag’s location.

This algorithm will essentially provide us with the sides of a triangle, with which we can calculate the location of the tag, we will be using the law of cosines to triangulate the location of the tag relative to the anchors.

\begin{algorithm}[H]
    \SetAlgoLined
    
    \Input{\textbf{Input}: Lengths of sides $(a, b, c)$}\\
    \Output{\textbf{Output}: Coordinates $(x, y)$} 

    % cos_a = (b * b + c*c - a * a) / (2 * b * c)
    % x = b * cos_a
    % y = b * cmath.sqrt(1 - cos_a * cos_a)
    
    $ \text{cos\_a} = \frac{{b^2 + c^2 - a^2}}{{2bc}} $\; \\
    $ x = b \cdot \text{cos\_a} $\; \\
    $ y = b \cdot \sqrt{1 - \text{cos\_a}^2} $\; \\
    
    \Return{$ (\text{round}(x.\text{real}, 1), \text{round}(y.\text{real}, 1)) $}\;
    
    \caption{Calculation of Coordinates using Law of Cosines}
\end{algorithm}

\newpage

\subsubsection{Requirements and Verification}
\begin{center}
\begin{tabular}{ | m{20em} || m{20em} | } 
  \hline
  Requirements & Verification  \\ 
  \hline
  \hline
  Utilize ToF or TDoA localization to create a triangle of known lengths with vertices defined by each UWB transceiver.
  & 
  Ensure the OWB is at an idle state such that the wheels are not spinning. Then, place the UWB Tag one meter away from the robot. Utilizing the visualization program by MakerFabs, we will test our algorithm by comparing the location that was calculated for the tag with the real-world location. Confirm that the proper location is displayed.
  \\ 
  \hline
\end{tabular}
\end{center}
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

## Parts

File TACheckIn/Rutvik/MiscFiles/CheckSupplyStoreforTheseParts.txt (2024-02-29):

Need to Check parts cabinet for the following components:

Cabinet 8, Drawer 19: LM338 Voltage Regulator - get 3

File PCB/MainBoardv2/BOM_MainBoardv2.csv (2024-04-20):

Reference | Value | Datasheet | Footprint | Qty | DNP
C1 | 10n | https://www.digikey.com/en/products/detail/kemet/C0603C103K4REC7867/8643658 | Capacitor_SMD:C_0603_1608Metric | 1
C2,C3,C11 | 1u | https://www.digikey.com/en/products/detail/yageo/CC0603KRX7R7BB105/2833611 | Capacitor_SMD:C_0603_1608Metric | 3
C4,C5,C6,C7,C13 | 100n | https://www.digikey.com/en/products/detail/yageo/CC0603KRX7R7BB104/302822 | Capacitor_SMD:C_0603_1608Metric | 5
C8,C9 | 10u | https://www.digikey.com/en/products/detail/samsung-electro-mechanics/CL10A106KQ8NNNC/3886696 | Capacitor_SMD:C_0603_1608Metric | 2
C10 | 22u | https://www.digikey.com/en/products/detail/samsung-electro-mechanics/CL21A226MQQNNNE/3886758 | Capacitor_SMD:C_0805_2012Metric | 1
C12,C14 | 20p | https://www.digikey.com/en/products/detail/kemet/C0603C200G8HAC7867/7946222 | Capacitor_SMD:C_0603_1608Metric | 2
Cboot? | 100nF | https://www.digikey.com/en/products/detail/kyocera-avx/KGM21NR71E104KT/1116281 | Capacitor_SMD:C_0805_2012Metric | 1
Cff? | 100pF | https://www.digikey.com/en/products/detail/kemet/C0805C101K3GAC7800/2211647 | Capacitor_SMD:C_0805_2012Metric | 1
Cin? | 15uF | https://www.digikey.com/en/products/detail/tdk-corporation/C2012X5R1V156M125AC/3951659 | Capacitor_SMD:C_0805_2012Metric | 1
Cinx? | 100nF | https://www.digikey.com/en/products/detail/knowles-syfer/0805J0500104KJT/7798603 | Capacitor_SMD:C_0805_2012Metric | 1
Cout? | 47uF | https://www.digikey.com/en/products/detail/murata-electronics/GRM32ER61C476KE15L/2548472 | Capacitor_SMD:C_1210_3225Metric | 1
D1,D2,D3,D4,D5,D6,D7,D8,D9 | LED | https://www.digikey.com/en/products/detail/w%C3%BCrth-elektronik/150060GS75000/4489898 | LED_SMD:LED_0603_1608Metric | 9
F1,F2,F3 | Polyfuse | https://www.digikey.com/en/products/detail/yageo/SMD2920B500TF-16/15212952 | Fuse:Fuse_2920_7451Metric | 3
FB1 | 120R | https://www.digikey.com/en/products/detail/murata-electronics/BLM18KG121TN1D/1982762 | Inductor_SMD:L_0603_1608Metric | 1
H1,H2,H3,H4 | MountingHole | ~ | MountingHole:MountingHole_5mm | 4
J1,J3 | Conn_02x03_Odd_Even | ~ | Connector_PinSocket_2.54mm:PinSocket_2x03_P2.54mm_Vertical | 2
J2 | USB_B_Micro | https://www.digikey.com/en/products/detail/amphenol-cs-fci/10118192-0002LF/6817756 | CustomFootprints:AMPHENOL_10118192-0002LF | 1
J4 | Conn_01x05_Pin | ~ | Connector_PinSocket_2.54mm:PinSocket_1x05_P2.54mm_Vertical | 1
J5,J11,J12,J14,J15,J17,J18,J20 | Conn_01x03_Socket | ~ | Connector_PinHeader_2.54mm:PinHeader_1x03_P2.54mm_Vertical | 8
J6,J8,J21,J22,J23 | Screw_Terminal_01x02 | https://www.digikey.com/en/products/detail/phoenix-contact/1017521/9346615 | CustomFootprints:1985195 | 5
J7,J9,J10 | Conn_01x04_Socket | ~ | Connector_PinHeader_2.54mm:PinHeader_1x04_P2.54mm_Vertical | 3
J13,J16,J19 | Conn_01x04_Socket | https://www.digikey.com/en/products/detail/jst-sales-america-inc./B4B-PH-K/768444?gad_source=1 | Connector_JST:JST_PH_B4B-PH-K_1x04_P2.00mm_Vertical | 3
L1 | 3.3uH | https://www.digikey.com/en/products/detail/vishay-dale/IHLP3232DZER3R3M01/2657469 | CustomFootprints:IHLP3232DZER3R3M01 | 1
R1,R2,R3,R4,R8,R9,R10,R11,R12,R13 | 1.5k | https://www.digikey.com/en/products/detail/yageo/RC0603JR-071K5L/726689 | Resistor_SMD:R_0603_1608Metric | 10
R5,R6,R7 | 10k | https://www.digikey.com/en/products/detail/stackpole-electronics-inc/RMCF0603JT10K0/1758104 | Resistor_SMD:R_0603_1608Metric | 3
Rfbb? | 10k | https://www.digikey.com/en/products/detail/vishay-dale/CRCW080510K0FKEA/1175751 | Resistor_SMD:R_0805_2012Metric | 1
Rfbt? | 73.2k | https://www.digikey.com/en/products/detail/panasonic-electronic-components/ERJ-6ENF7322V/111652 | Resistor_SMD:R_0805_2012Metric | 1
Rff? | 20k | https://www.digikey.com/en/products/detail/vishay-dale/CRCW080520K0FKEA/1175783 | Resistor_SMD:R_0805_2012Metric | 1
Rpg? | 100k | https://www.digikey.com/en/products/detail/vishay-dale/CRCW0805100KFKEA/1175865 | Resistor_SMD:R_0805_2012Metric | 1
SW1 | SW_Push | https://www.digikey.com/en/products/detail/omron-electronics-inc-emc-div/B3S-1000/20686 | Button_Switch_SMD:SW_SPST_B3S-1000 | 1
SW2 | Toggle | https://mm.digikey.com/Volume0/opasdata/d220001/medias/docus/2910/MTx%20Series%20Catalog.pdf | CustomFootprints:MTM8206NRA | 1
SW3 | Slide | https://www.digikey.com/en/products/detail/cw-industries/GF-161-0005/4089836 | CustomFootprints:SW_GF-161-0005 | 1
TP1 | 5V | https://www.digikey.com/en/products/detail/keystone-electronics/5000/255326 | TestPoint:TestPoint_Keystone_5000-5004_Miniature | 1
TP2 | 3.3V | https://www.digikey.com/en/products/detail/keystone-electronics/5000/255326 | TestPoint:TestPoint_Keystone_5000-5004_Miniature | 1
TP3,TP11,TP12,TP13 | White | https://www.digikey.com/en/products/detail/keystone-electronics/5002/255328 | TestPoint:TestPoint_Keystone_5000-5004_Miniature | 4
TP4,TP5,TP6,TP7,TP9,TP10 | Orange | https://www.digikey.com/en/products/detail/keystone-electronics/5003/362668 | TestPoint:TestPoint_Keystone_5000-5004_Miniature | 6
TP8 | 12V | https://www.digikey.com/en/products/detail/keystone-electronics/5000/255326 | TestPoint:TestPoint_Keystone_5000-5004_Miniature | 1
TP14 | GND | https://www.digikey.com/en/products/detail/keystone-electronics/5001/255327 | TestPoint:TestPoint_Keystone_5000-5004_Miniature | 1
U1 | AZ1117-3.3 | https://www.digikey.com/en/products/detail/diodes-incorporated/AZ1117CD-3-3TRG1/4470979 | Package_TO_SOT_SMD:TO-252-2 | 1
U2 | STM32F103C8T6TR | https://www.st.com/resource/en/datasheet/stm32f103c8.pdf | Package_QFP:LQFP-48_7x7mm_P0.5mm | 1
U3 | SN74HCS4075PWR | https://www.digikey.com/en/products/detail/texas-instruments/SN74HCS4075PWR/11635670 | CustomFootprints:SN74HCS4075PWR | 1
U4 | TPS56637RPA | https://www.digikey.com/en/products/detail/texas-instruments/TPS56637RPAR/10715537 | CustomFootprints:RPA0010A | 1
Y1 | 8MHz Crystal | https://www.digikey.com/en/products/detail/ecs-inc/ECS-080-20-4X-DU/2781927 | Crystal:Crystal_HC49-U_Vertical | 1

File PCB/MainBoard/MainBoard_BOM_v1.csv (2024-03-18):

Reference | Value | Datasheet | Footprint | Qty | DNP
C1,C2,C10,C11,C16,C17 | 10u | ~ | Capacitor_SMD:C_1206_3216Metric_Pad1.33x1.80mm_HandSolder | 6
C3,C4,C5 | 0.1uF | ~ | Capacitor_SMD:C_1206_3216Metric_Pad1.33x1.80mm_HandSolder | 3
C6,C7,C12,C13,C18,C19 | 100n | ~ | Capacitor_SMD:C_1206_3216Metric_Pad1.33x1.80mm_HandSolder | 6
C8,C9,C14,C15,C20,C21 | 33u | ~ | Capacitor_SMD:C_1206_3216Metric_Pad1.33x1.80mm_HandSolder | 6
D1,D2,D3,D4 | LED | ~ | LED_THT:LED_D3.0mm_Clear | 4
H1,H2,H3,H4 | MountingHole | ~ | MountingHole:MountingHole_5mm | 4
J4,J8,J9,J17,J21 | Conn_01x02_Socket | ~ | Connector_Wire:SolderWire-0.5sqmm_1x02_P4.8mm_D0.9mm_OD2.3mm | 5
J5,J6,J7,J14 | Conn_01x03_Socket | ~ | Connector_PinHeader_2.54mm:PinHeader_1x03_P2.54mm_Vertical | 4
J10,J11 | Conn_01x06_Socket | ~ | Connector_PinHeader_2.54mm:PinHeader_1x06_P2.54mm_Vertical | 2
J12,J18,J19,J20 | Conn_01x04_Socket | ~ | -- mixed values -- | 4
JP1,JP2,JP3 | SolderJumper_2_Open | ~ | Jumper:SolderJumper-2_P1.3mm_Open_TrianglePad1.0x1.5mm | 3
L1 | 4.7u | ~ | Inductor_SMD:L_1008_2520Metric | 1
L2 | 6.8u | ~ | Inductor_SMD:L_1008_2520Metric | 1
L3 | 5.6u | ~ | Inductor_SMD:L_1008_2520Metric | 1
R1,R2,R3,R10 | 4.7k | ~ | Resistor_THT:R_Axial_DIN0207_L6.3mm_D2.5mm_P7.62mm_Horizontal | 4
R4 | 31.1k | ~ | Resistor_THT:R_Axial_DIN0207_L6.3mm_D2.5mm_P7.62mm_Horizontal | 1
R5,R7,R9 | 10k | ~ | Resistor_THT:R_Axial_DIN0207_L6.3mm_D2.5mm_P7.62mm_Horizontal | 3
R6 | 53.6k | ~ | Resistor_THT:R_Axial_DIN0207_L6.3mm_D2.5mm_P7.62mm_Horizontal | 1
R8 | 52.3k | ~ | Resistor_THT:R_Axial_DIN0207_L6.3mm_D2.5mm_P7.62mm_Horizontal | 1
SW1 | SW_Push | ~ | Button_Switch_THT:SW_PUSH_6mm_H7.3mm | 1
TP1,TP2,TP3,TP4,TP5,TP6 | TestPoint | ~ | Connector_PinHeader_2.54mm:PinHeader_1x01_P2.54mm_Vertical | 6
U1,U2,U5 | TPS56339DDC | https://www.ti.com/lit/ds/symlink/tps56339.pdf | Package_TO_SOT_SMD:SOT-23-6 | 3
U3 | STM32F103C8Tx | https://www.st.com/resource/en/datasheet/stm32f103c8.pdf | Package_QFP:LQFP-48_7x7mm_P0.5mm | 1
U4,U6 | CD74HC00_N_14 |  | Package_DIP:DIP-14_W7.62mm_LongPads | 2

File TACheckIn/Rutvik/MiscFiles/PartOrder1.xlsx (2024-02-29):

Part order #1
Part | Cost | Quantity | Total Cost | Link | Grand Total
4" Omni-wheels | $26.00 | $3.00 | $78.00 | Link (https://www.andymark.com/products/4-in-duraomni-wheel) | $129.96
Modern Robotics 12VDC Motor | $14.99 | $3.00 | $44.97 | Link (https://www.gobilda.com/modern-robotics-12vdc-motor/)
JST-XH Female - JST-XH Female | $6.99 | $1.00 | $6.99 | Link (https://www.amazon.com/Hxchen-2-54mm-Pitch-Female-Adapter/dp/B07W3K71X3)
 |  |  | $0.00 | Link
 |  |  | $0.00 | Link
 |  |  | $0.00 | Link
 |  |  | $0.00 | Link
 |  |  | $0.00 | Link
 |  |  | $0.00 | Link
 |  |  | $0.00 | Link
 |  |  | $0.00 | Link
 |  |  | $0.00 | Link
 |  |  | $0.00 | Link
 |  |  | $0.00 | Link
 |  |  | $0.00
 |  |  | $0.00
 |  |  | $0.00
 |  |  | $0.00
 |  |  | $0.00
 |  |  | $0.00
 |  |  | $0.00
 |  |  | $0.00
 |  |  | $0.00
 |  |  | $0.00
 |  |  | $0.00
 |  |  | $0.00

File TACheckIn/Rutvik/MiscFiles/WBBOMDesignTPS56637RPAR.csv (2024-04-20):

Part | Manufacturer | Part Number | Quantity | Price ($) | Footprint (mm²) | Description
Rfbb | Vishay-Dale | CRCW080510K0FKEA | 1 | 0.01 | 6.75 | Resistance: 10 kΩ Tolerance: 1.0% Power: 125 mW
Rfbt | Panasonic | ERJ-6ENF7322V | 1 | 0.01 | 6.75 | Resistance: 73.2 kΩ Tolerance: 1.0% Power: 125 mW
Cinx | MuRata | GRM21BR71H104KA01L | 1 | 0.03 | 6.75 | Cap: 100 nF Total Derated Cap: 91 nF VDC: 50 V ESR: 1 mΩ Package: 0805
U1 | Texas Instruments | TPS56637RPAR | 1 | 0.8 | 16
Rpg | Vishay-Dale | CRCW0805100KFKEA | 1 | 0.01 | 6.75 | Resistance: 100 kΩ Tolerance: 1.0% Power: 125 mW
Cin | TDK | C2012X5R1V156M125AC | 1 | 0.2 | 6.75 | Cap: 15 µF Total Derated Cap: 1.2 µF VDC: 35 V ESR: 1.67 mΩ Package: 0805
Cout | MuRata | GRM32ER61C476KE15L | 1 | 0.17 | 14.7 | Cap: 47 µF Total Derated Cap: 32 µF VDC: 16 V ESR: 3.04 mΩ Package: 1210
L1 | Vishay-Dale | IHLP3232DZER3R3M01 | 1 | 0.71 | 111.83 | L: 3.3 µH DCR: 17.7 mΩ IDC: 9.2 A
Cboot | AVX | 08053C104KAT2A | 1 | 0.01 | 6.75 | Cap: 100 nF Total Derated Cap: 100 nF VDC: 25 V ESR: 280 mΩ Package: 0805
Cff | Kemet | C0805C101K3GACTU | 1 | 0.03 | 6.75 | Cap: 100 pF Total Derated Cap: 100 pF VDC: 25 V ESR: 0 Ω Package: 0805
Rff | Vishay-Dale | CRCW080520K0FKEA | 1 | 0.01 | 6.75 | Resistance: 20 kΩ Tolerance: 1.0% Power: 125 mW

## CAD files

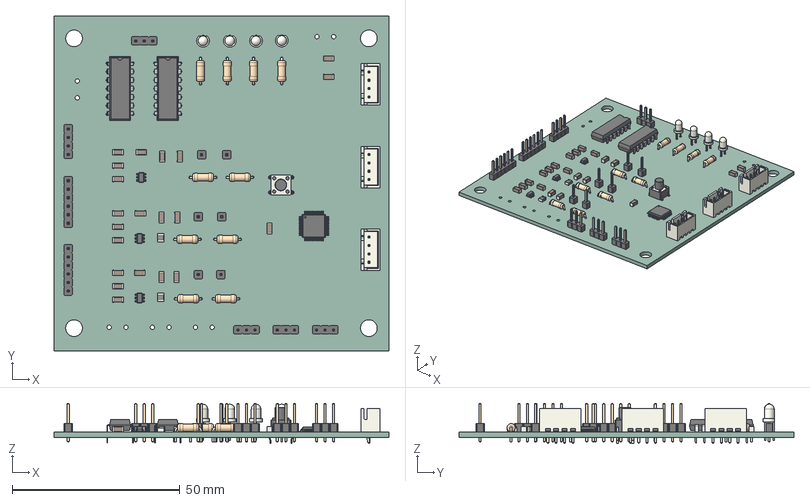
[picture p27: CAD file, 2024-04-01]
PCB/MainBoard/MainBoard.step
100.0 x 100.0 x 12.0 mm
SOT_23_6 x 3
R_Axial_DIN0207_L63mm_D25mm_P762mm_Horizontal x 10
C_1206_3216Metric x 21
PinHeader_1x01_P254mm_Vertical x 6
PinHeader_1x04_P254mm_Vertical
PinHeader_1x03_P254mm_Vertical x 4
LED_D3.0mm_Clear x 4
SW_PUSH_6mm_h7.3mm
LQFP_48_7x7mm_P05mm
L_1008_2520Metric x 2
JST_B4B_XH_A x 3
PinHeader_1x06_P254mm_Vertical x 2
DIP-14_W7.62mm x 2
_autosave-MainBoard_PCB

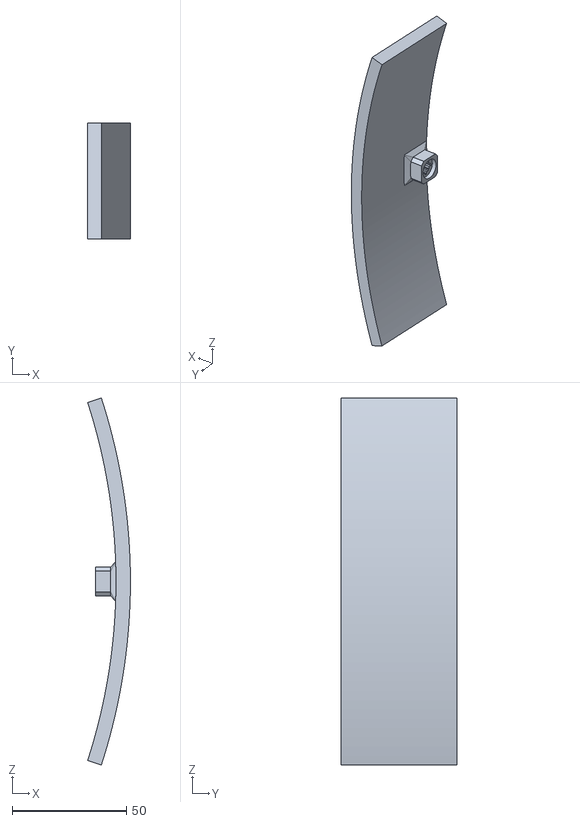
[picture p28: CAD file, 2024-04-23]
TACheckIn/Rutvik/3D_Printing/Final1/MainBodyLimitSwitch.stl
18.8 x 50.8 x 160.9

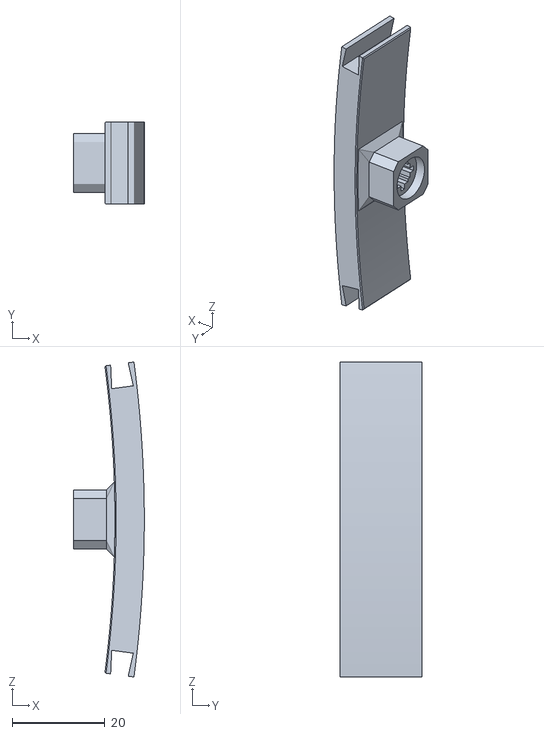
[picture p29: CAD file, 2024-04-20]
TACheckIn/Rutvik/3D_Printing/LimitSwitchMainBodyv5.stl
15.2 x 17.8 x 68.0

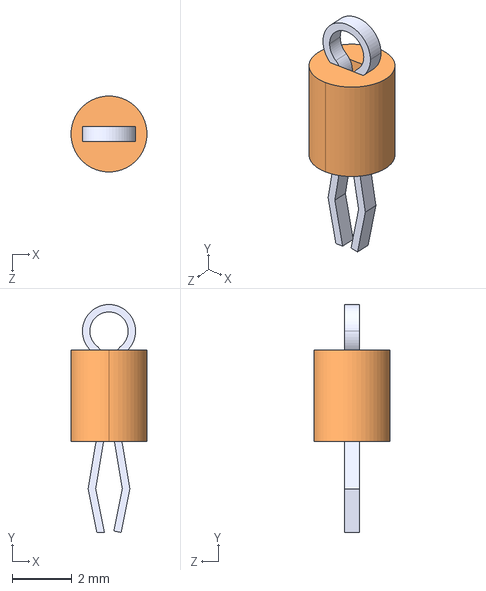
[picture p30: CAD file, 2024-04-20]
PCB/LibraryFiles/5003/5003.step
2.54 x 7.62 x 2.54 mm

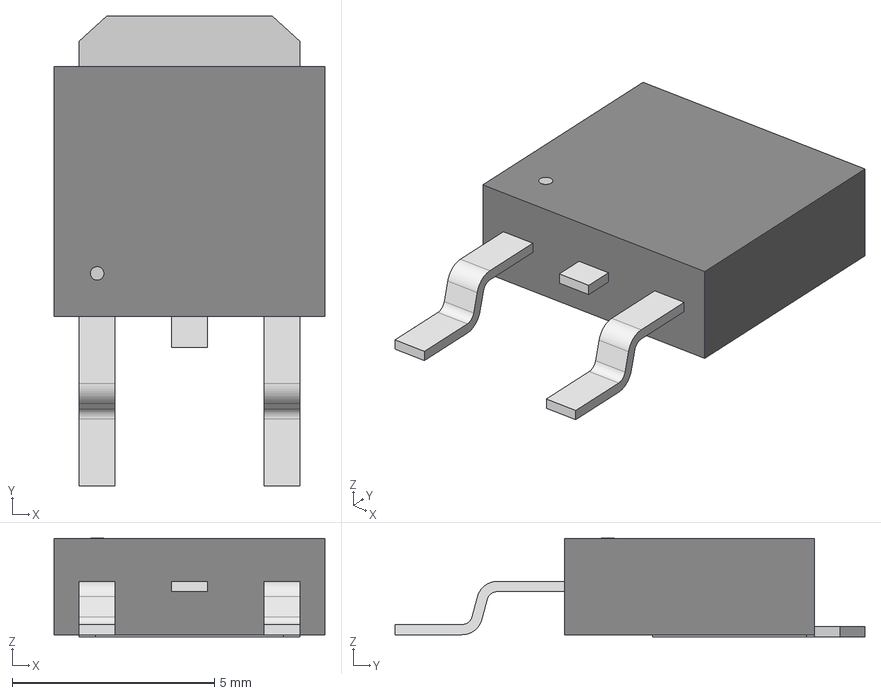
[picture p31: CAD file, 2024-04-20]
PCB/LibraryFiles/AZ1117CD_3_3TRG1/TO252-2-3_3V_DIO.step
6.71 x 11.6 x 2.44 mm

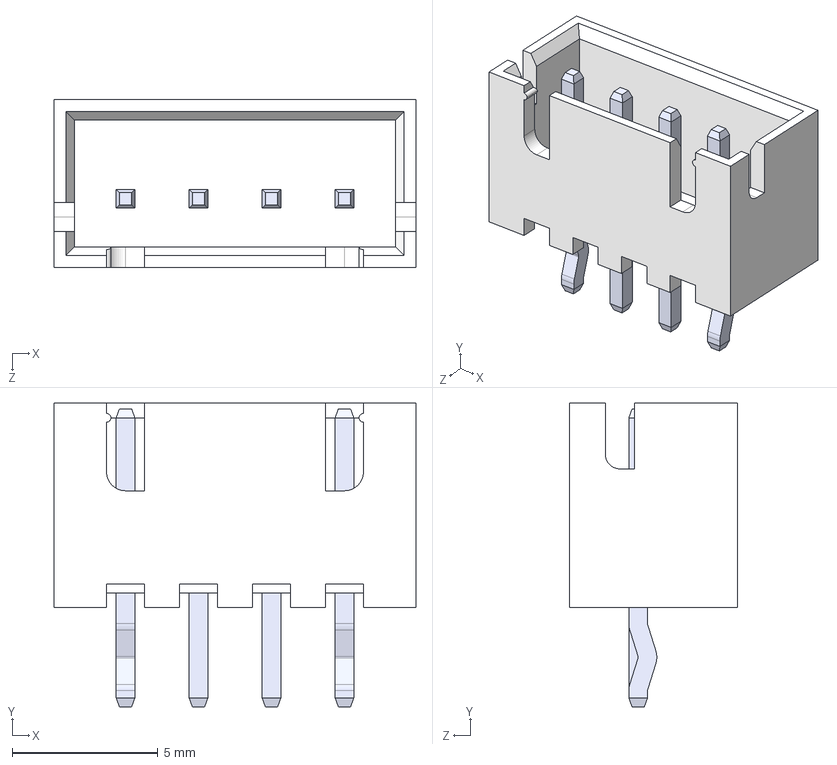
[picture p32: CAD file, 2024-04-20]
PCB/LibraryFiles/B4B_XH_A/B4B-XH-A.step
12.4 x 10.4 x 5.75 mm

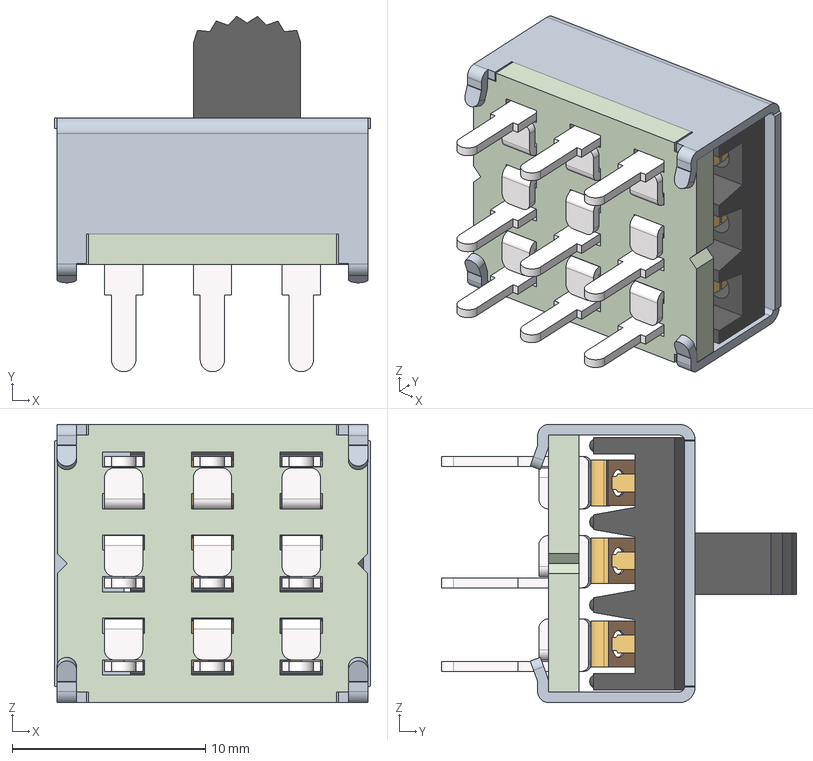
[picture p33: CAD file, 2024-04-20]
PCB/LibraryFiles/GF_161_0005/GF-161-0005_3D Model.stp
16.4 x 18.4 x 14.4 mm

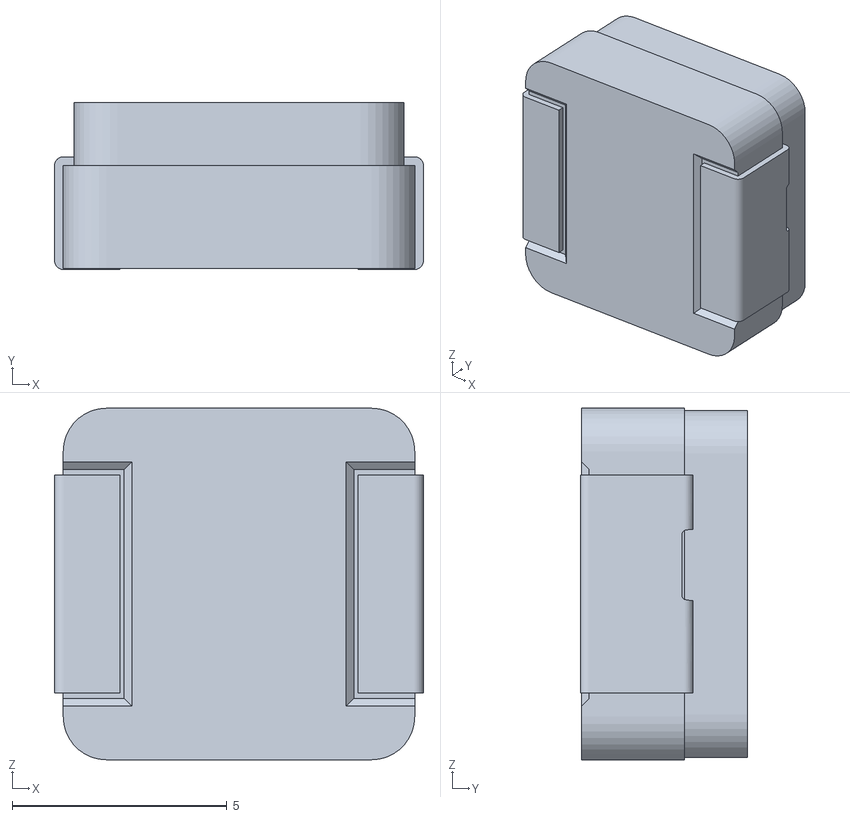
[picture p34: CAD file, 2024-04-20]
PCB/LibraryFiles/IHLP3232DZER3R3M01/IHLP3232DZ.stl
8.60 x 3.90 x 8.19

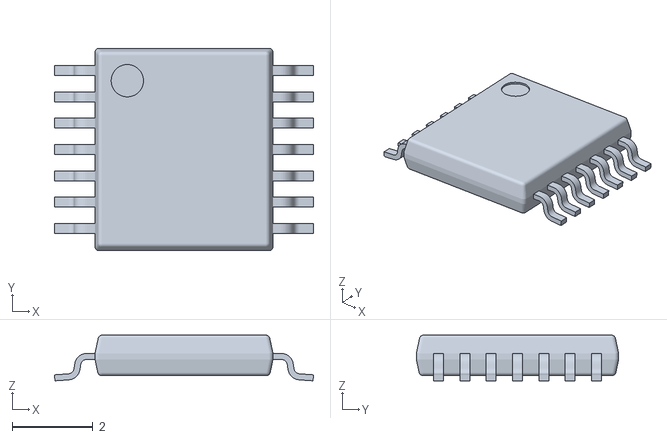
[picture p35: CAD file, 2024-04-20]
PCB/LibraryFiles/SN74HCS4075PWR/PW0014A.stl
6.40 x 5.00 x 1.13

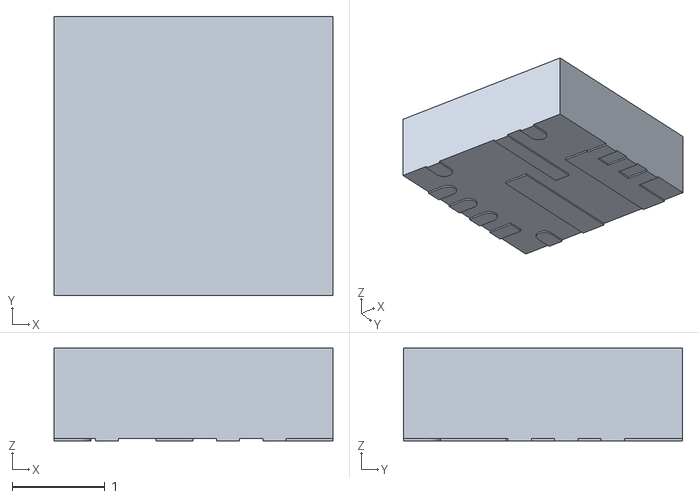
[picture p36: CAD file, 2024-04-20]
PCB/LibraryFiles/TPS56637RPAR/RPA0010A.stl
3.00 x 3.00 x 1.00

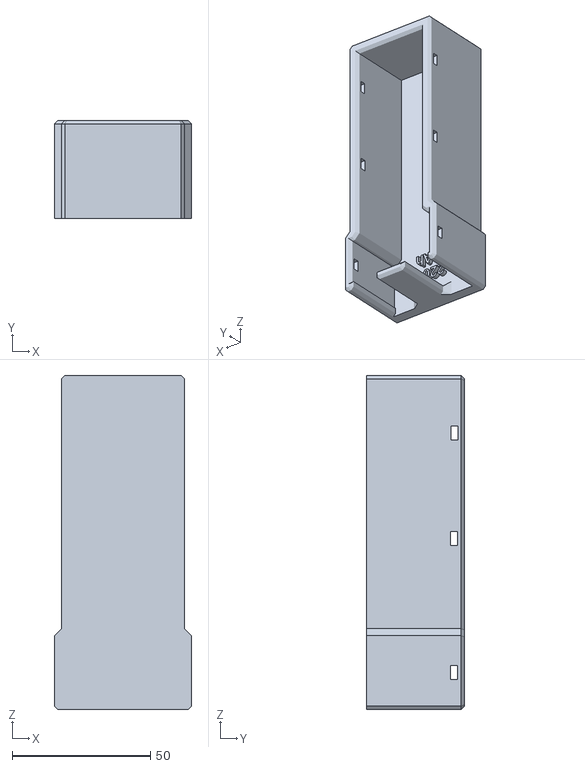
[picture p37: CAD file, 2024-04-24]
TACheckIn/Rutvik/3D_Printing/Final1/BatteryHousing.stl
49.5 x 35.6 x 120.7

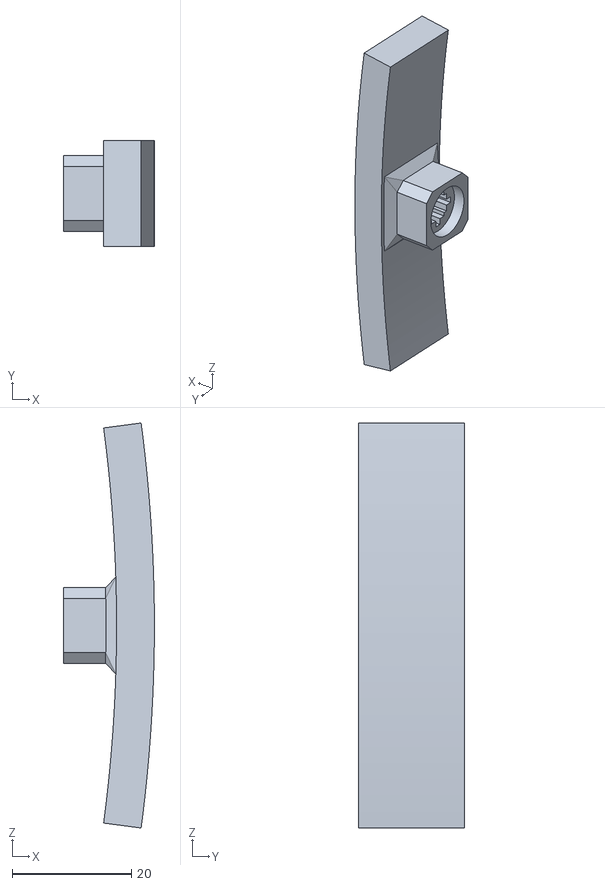
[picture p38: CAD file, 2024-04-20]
TACheckIn/Rutvik/3D_Printing/LimitSwitchBumper.stl
15.2 x 17.8 x 68.0

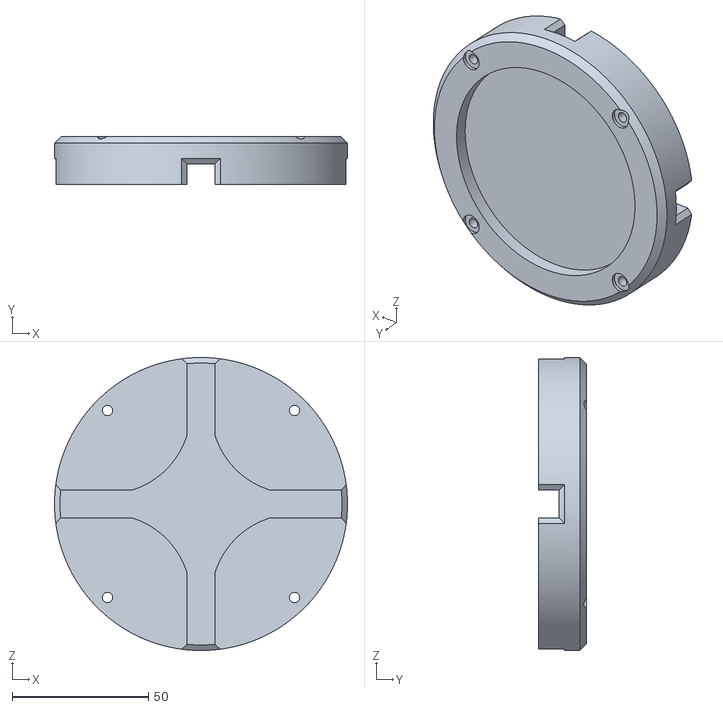
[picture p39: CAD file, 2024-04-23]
TACheckIn/Rutvik/3D_Printing/Final1/OxygenTankStandoff.stl
107.4 x 17.8 x 107.4

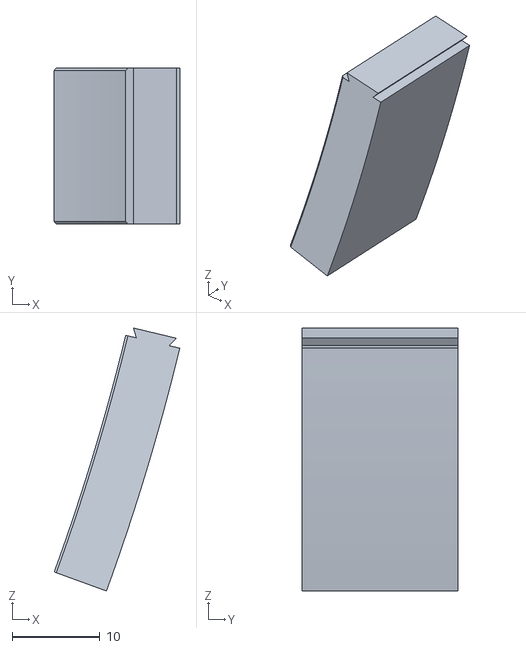
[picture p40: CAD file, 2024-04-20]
TACheckIn/Rutvik/3D_Printing/LimitSwitchInterlocking2.stl
14.3 x 17.8 x 30.0

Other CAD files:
TACheckIn/Rutvik/3D_Printing/LimitSwitchBumperInterlocking1.stl
TACheckIn/Rutvik/3D_Printing/LimitSwitchBody3_v5.stl
PCB/LibraryFiles/1017521/1017521.step
PCB/LibraryFiles/AZ1117CD_3_3TRG1/TO252-2-3_3V_DIO.stl
TACheckIn/Aidan/Bumper v15.f3d
TACheckIn/Rutvik/3D_Printing/LimitSwitchConnector.stl
TACheckIn/Rutvik/3D_Printing/LimitSwitchConnectorv2.stl
TACheckIn/Rutvik/3D_Printing/LimitSwitchScrewTerminal.stl
TACheckIn/Rutvik/3D_Printing/LimitSwitchScrewTerminalv2.stl
TACheckIn/Rutvik/3D_Printing/LimitSwitchScrewTerminalv3.stl
TACheckIn/Rutvik/3D_Printing/LimitSwitchScrewTerminalv4.stl
TACheckIn/Rutvik/3D_Printing/LimitSwitchScrewTerminalv5.stl

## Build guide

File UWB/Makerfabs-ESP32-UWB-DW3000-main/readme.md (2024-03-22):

# Makerfabs ESP32 UWB DW3000

**The DW3000 library in this repository was developed by NConcepts, not Makerfabs.  Makerfabs is simply responsible for maintaining the repository.**

```c++
/*
Version:        V1.2
Author:            Vincent
Create Date:    2022/8/1
Note:
    2023/5/5     V1.2:The routines that can be used are placed in 
                    the example folder separately, with instructions 
                    added.
    2023/3/18    V1.1:Modify the SPI operating frequency in the library.
                      Added software reset to demo.
*/
```

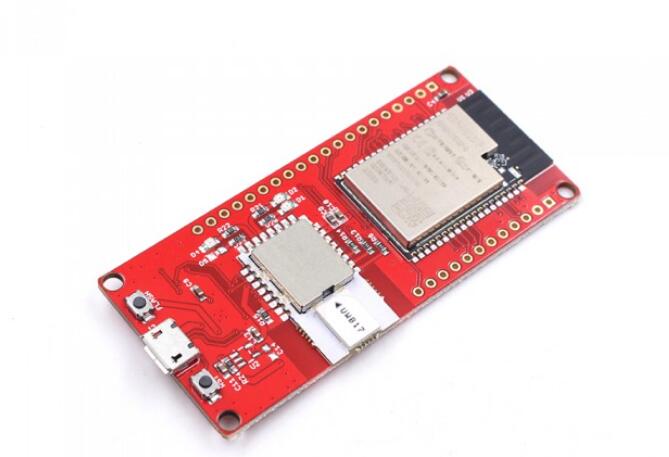
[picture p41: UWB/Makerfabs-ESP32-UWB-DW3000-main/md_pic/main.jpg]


[TOC]

# Makerfabs

[Makerfabs home page](https://www.makerfabs.com/)

[Makerfabs Wiki](https://wiki.makerfabs.com/)

# Makerfabs ESP32 UWB DW3000

## Intruduce

Product Link ：[esp32-uwb-dw3000](https://www.makerfabs.com/esp32-uwb-dw3000.html) 

Wiki Link : [ESP32 UWB DW3000](https://wiki.makerfabs.com/ESP32_DW3000_UWB.html)

Makerfabs ESP32 UWB contains an ESP32 and a DW3000 chip.

Ultra-wideband (UWB) is a short-range, wireless communication protocol that operates through radio waves, enables secure reliable ranging and precision sensing, creating a new dimension of spatial context for wireless devices.

Makerfabs ESP32 UWB module, which is based on IC DecaWave DW1000, has been greatly popular and liked by many Makers. And many customers ask us for the newest DW3000 version, after long-term comparison & testing, now it's available!~

Compares to the DWM1000, the DWM3000 has advantages as below:

1. Most important: Interoperable with Apple U1 chip, that makes it possible to work with the Apple system;
2. Fully aligned with FiRa™ PHY, MAC, and certification development, which make it more suitable for further applications;
3. Much lower Power consumption, almost 1/3 of DWM1000;
4. Supports UWB channels 5 (6.5 GHz) and 9 (8 GHz), while DWM1000 does not support Channel 9;

## Feature

- Integrated ESP32 2.4G WiFi and Bluetooth.
- DW3000 UWB module.

# Usage

## Install Library

**The library is provided by the customer. It was not developed by Makerfabs.**

Copy "Dw3000" to Arduino library directory.

## Example

**The codes are provided by the customer, which can realize the basic usage.**

## simple_test

The appearance of the test program, simple send and receive data. TX sends, RX receives the message.

## range

Simple test program, respectively download range_tx and range_rx. range_rx's serial port outputs distance.

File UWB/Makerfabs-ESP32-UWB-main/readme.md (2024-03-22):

# Makerfabs ESP32 UWB & Display

```c++
/*
Version:		V4.3
Author:			Vincent
Create Date:	2021/11/6
Note:
	2021/12/9 	V2.0:Add a Indoor Positioning demo.
	2022/6/29 	V2.1:Add DW3000 library.
	2022/8/1  	V3.0:Provides a library available for high-power versions. Move DW3000 to other 		  					     repositories.
	2022/9/6	V3.1:Added changes to the high-power version.
	2022/10/26 	V4.0:Add new version with SSD1306
	2022/11/15	V4.1:Change library name to mf_DW1000.zip
	2022/12/29	V4.2: Change wiki link
	2023/1/3	V4.3: Change directory name.
*/
```
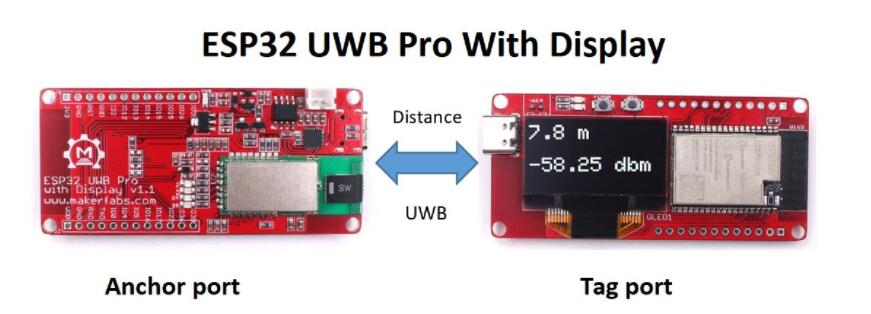
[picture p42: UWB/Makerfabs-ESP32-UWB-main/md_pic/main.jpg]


[toc]

# Makerfabs

[Makerfabs home page](https://www.makerfabs.com/)

[Makerfabs Wiki](https://wiki.makerfabs.com/)

# Makerfabs ESP32 UWB Serials
## Intruduce

ESP32 UWB : [esp32-uwb-ultra-wideband](https://www.makerfabs.com/esp32-uwb-ultra-wideband.html) 

ESP32 UWB Pro : [esp32-uwb-high-power](https://www.makerfabs.com/esp32-uwb-high-power-120m.html)

ESP32 UWB Pro with Display : [ESP32 UWB Pro with Display](https://www.makerfabs.com/esp32-uwb-pro-with-display.html)

Wiki Link : [ESP32 UWB Pro with Display](https://wiki.makerfabs.com/ESP32_UWB_Pro_with_Display.html) 

Ultra-wideband (UWB) is a short-range, wireless communication protocol that operates through radio waves, enables secure reliable ranging and precision sensing, creating a new dimension of spatial context for wireless devices.

This new ESP32 UWB pro with display is the updated version of ESP32 UWB Pro, with the following new spec:

- On-board OLED, 1.3” 128*64, so the distance results can be directly displayed
- Lipo battery charger& connector, so this module can work separately with batteries
- Update UWB position, so the module can be directly installed into a case

| | **UWB Basic** | **UWB Pro** | **UWB Pro with Display** | **UWB DW3000** |
| --------------------- | ------------------------------------------------------------ | ------------------------------------------------------------ | ------------------------ | ------------------------------------------------------------ |
| CPU                   | ESP32-WROOM/WROVER                                           | ESP32-WROVER                                                 | ESP32-WROVER             | ESP32-WROOM/WROVER                                           |
| Core UWB              | DW1000                                                       | DW1000                                                       | DW1000                   | DW3000                                                       |
| Screen                | N                                                            | N                                                            | Y                        | N                                                            |
| Measuring distance(m) | 45                                                           | 200                                                          | 200                      | 20                                                           |
| Battery Socket        | N                                                            | N                                                            | Y                        | N                                                            |
| UWB Channel           | 2/5                                                          | 2/5                                                          | 2/5                      | 5/9                                                          |
| Apple Interoperable   | N                                                            | N                                                            | N                        | Y                                                            |
| Suitable for          | Normal Testing                                               | Long distance needed                                         | Long distance needed     | Product development                                          |

### UWB Basic

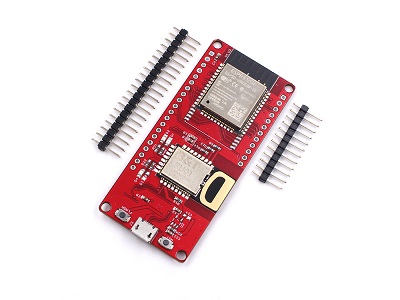
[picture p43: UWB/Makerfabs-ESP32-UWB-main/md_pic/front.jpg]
front


### UWB Pro

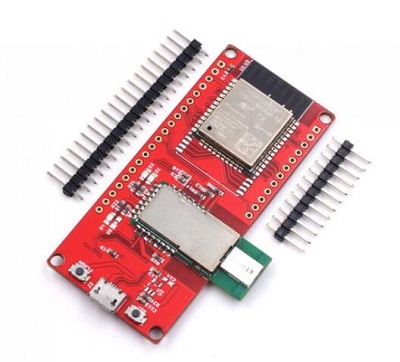
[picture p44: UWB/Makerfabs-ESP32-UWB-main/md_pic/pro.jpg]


### UWB Pro with Display

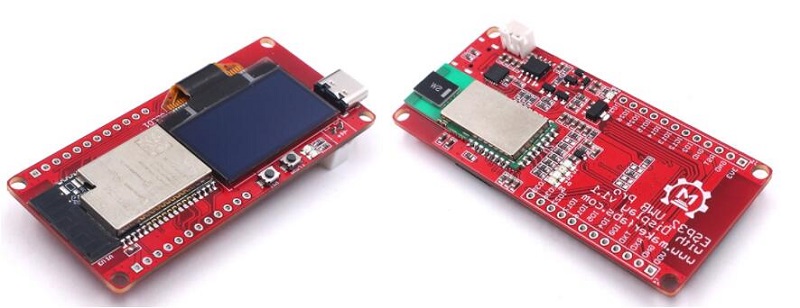
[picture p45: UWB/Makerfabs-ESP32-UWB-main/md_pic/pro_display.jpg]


# Example

## Compiler Options

**If you have any questions，such as how to install the development board, how to download the code, how to install the library. Please refer to :[Makerfabs_FAQ](https://github.com/Makerfabs/Makerfabs_FAQ)**

- Install board : ESP32 .
- Rename mf_DW1000.zip to DW1000.zip and install it.
- Install library : Adafruit_SSD1306
- Upload code, select board "ESP32 DEV"

**This library was modified from the [DW1000](https://github.com/thotro/arduino-dw1000) library to work with the Makerfabs hardware. **

**Please download the latest version from our Github.**

## Example List

### uwb_tag

*For ESP32 UWB and ESP32 UWB Pro*

Distance to the receiving end of the test. You need an anchor point to receive data.

### uwb_tag_display

*For ESP32 UWB Pro with display*

Distance to the receiving end of the test. You need an anchor point to receive data.

### anchor

*For ESP32 UWB and ESP32 UWB Pro*

Distance test anchor point.

### anchor_display

*For ESP32 UWB Pro with display*

Distance test anchor point.

### Indoor positioning

*For ESP32 UWB and ESP32 UWB Pro*

Three UWB modules were used for indoor plane positioning. Data is transmitted through UDP protocol and graphically displayed in Python. 

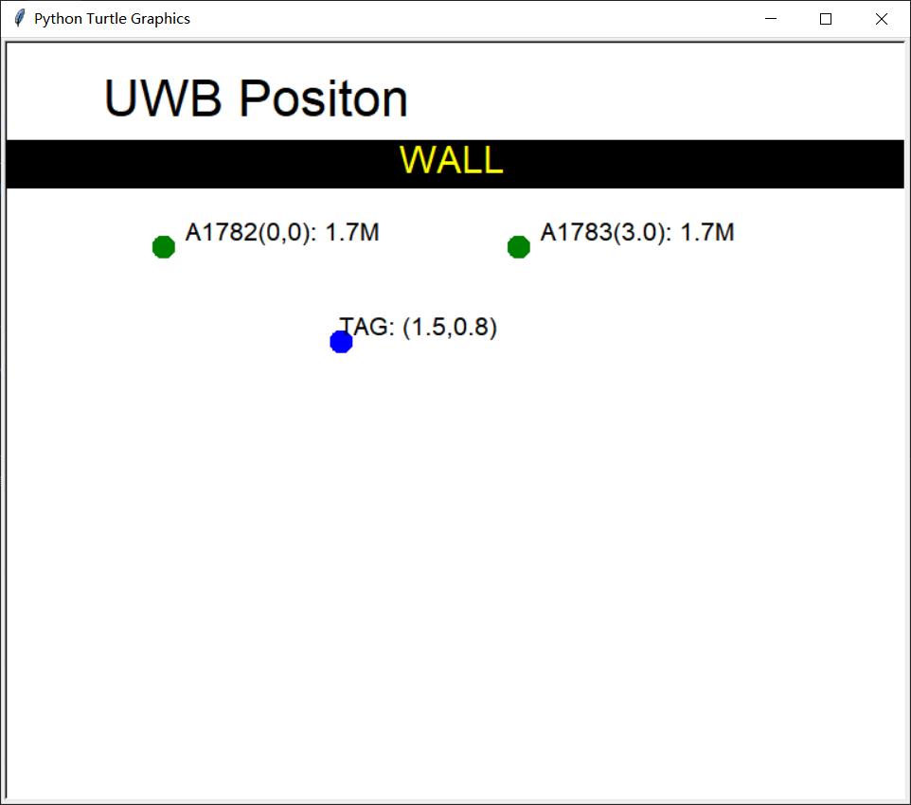
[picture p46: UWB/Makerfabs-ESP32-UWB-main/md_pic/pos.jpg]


The law of cosines is used to calculate tag coordinates.

```python
def tag_pos(a, b, c):
    # p = (a + b + c) / 2.0
    # s = cmath.sqrt(p * (p - a) * (p - b) * (p - c))
    # y = 2.0 * s / c
    # x = cmath.sqrt(b * b - y * y)
    cos_a = (b * b + c*c - a * a) / (2 * b * c)
    x = b * cos_a
    y = b * cmath.sqrt(1 - cos_a * cos_a)

    return round(x.real, 1), round(y.real, 1)
```

## Pin Define

### ESP32 UWB and ESP32 UWB Pro

```c++
#define SPI_SCK 18
#define SPI_MISO 19
#define SPI_MOSI 23

#define DW_CS 4
#define PIN_RST 27
#define PIN_IRQ 34
```

### ESP32 Pro with display

```c++
#define SPI_SCK 18
#define SPI_MISO 19
#define SPI_MOSI 23

#define UWB_SS 21   // spi select pin
#define UWB_RST 27  // reset pin
#define UWB_IRQ 34  // irq pin

#define I2C_SDA 4	//I2C screen ssd1306
#define I2C_SCL 5
```

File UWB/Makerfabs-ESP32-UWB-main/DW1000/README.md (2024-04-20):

# arduino-dw1000









A library that offers basic functionality to use Decawave's DW1000 chips/modules with Arduino
(see https://www.decawave.com/products/dwm1000-module).

Project state
-------------

**Development:**
There is **no active development** by the owner *thotro*.

This library is currently (2019) **not actively maintained**.

Anyway you can create pull requests if you found a bug or developed a new feature. They maybe help others.

**TODOs:**
* Fill wiki: https://github.com/thotro/arduino-dw1000/wiki
* MAC and frame filtering, error handling
* Sleep/power optimizations
* Refactor `DW1000Mac`
* Refactor `DW1000Ranging`
* Refactor `DW1000Device`
* Update examples (complete todos in header notice)

**What can I do with this lib?:**
Stable transmission of messages between two modules is possible. The code for device tuning is working as well, hence different modes of operation can be chosen. As frame filtering (i.e. via MAC conforming messages) is partially implemented yet, internal features of the chip for node addressing and auto-acknowledgement of messages can not be used. This is part of a future milestone. For now, if acknowledgements are required, they have to be sent manually and node addresses have to be encoded in the message payload and processed by the host controller.

**General notice:**
* The documentation https://github.com/thotro/arduino-dw1000/tree/master/extras/doc is manually generated and maybe out of date.
* Datasheet and application notices are available at https://www.decawave.com/ (require free registration).

Installation
------------

**Requires c++11 support**, Arduino IDE >= 1.6.6 support c++11.

 1. Get a ZIP file of the master branch or the latest release and save somewhere on your machine.
 2. Open your Arduino IDE and goto _Sketch_ / _Include Library_ / _Add .ZIP Library..._
 3. Select the downloaded ZIP file of the DW1000 library
 4. You should now see the library in the list and have access to the examples in the dedicated section of the IDE

Note that in version 1.6.6 of your Arduino IDE you can get the library via the Arduino library manager.

Contents
--------

 * [Project structure](../../wiki/Project-structure)
 * [Features and design intentions](../../wiki/Features)
 * [Testbed and Adapter board](../../wiki/Testbed-and-Adapter-board)
 * [Projects, Media, Links](../../wiki/Projects)
 * [Benchmarks](../../wiki/Benchmarks)
 * API docs
   * [HTML](https://cdn.rawgit.com/thotro/arduino-dw1000/master/extras/doc/html/index.html)
   * [PDF](https://cdn.rawgit.com/thotro/arduino-dw1000/master/extras/doc/DW1000_Arduino_API_doc.pdf)

Usage
-----

General usage of the DW1000 library is depicted below. Please see the Arduino test example codes (described in the [project structure](../../wiki/Project-structure)) for more up-to-date and operational reference usage. 

At the moment the library contains two types:
 * **DW1000:**
 State: stable.
 The statically accessible entity to work with your modules. Offers a variety of configuration options and manages module states and actions. 
 
 * **DW1000Time:**
 State: stable.
 Container entities that handle DW1000 specific timing values. These are required to allow accurate timestamps and time based computations; they aid in avoiding potential precision and capacity problems of standard number formats in Arduino and basically are wrapper objects for 64-bit signed integer data types; most importantly they take care of all bit-to-time-and-distance (and vice versa) conversions.
 
 * **DW1000Ranging:**
 State: prototype.
 Contain all functions which allow to make the ranging protocole. 
 
 * **DW1000Device:**
 State: prototype.
 Contain all informations (long address, short ephemeral address, DW1000Time of transition)  about a distant device (anchor or tag) on the same network.
 
 * **DW1000Mac:**
 State: prototype.
 This class is a child of the DW1000Device class and allow to generate the MAC frame for his DW1000Device parent.

```Arduino
#include <DW1000.h>
...
// init with interrupt line and optionally with reset line
DW1000.begin(irq_pin[, rst_pin]);
// select a specific chip via a chip select line
DW1000.select(cs_pin);
// or use DW1000.reselect(cs_pin) to switch to previously selected chip
...
// open a device configuration sessions
DW1000.newConfiguration();
// configure specific aspects and/or choose defaults
DW1000.setDefaults();
DW1000.setDeviceAddress(5);
DW1000.setNetworkId(10);
// modes that define data rate, frequency, etc. (see API docs)
DW1000.enableMode(DW1000.MODE_LONGDATA_RANGE_LOWPOWER);
// ... and other stuff - finally upload to the module.
DW1000.commitConfiguration();
...
// set some interrupt callback routines
DW1000.attachSentHandler(some_handler_function);
DW1000.attachReceivedHandler(another_handler_function);
...
// open a new transmit session
DW1000.newTransmit();
// configure specific aspects and/or choose defaults
DW1000.setDefaults();
DW1000.setData(some_data);
DW1000Time delayTime = DW1000Time(100, DW1000Time::MILLISECONDS);
[DW1000Time futureTimestamp = ]DW1000.setDelay(delayTime);
// ... and other stuff - finally start the transmission
DW1000.startTransmit();
...
// similar for a receiving session, like so ...
DW1000.newReceive();
DW1000.setDefaults();
// so we don't need to restart the receiver manually each time
DW1000.receivePermanently(true);
// ... and other stuff - finally start awaiting messages
DW1000.startReceive();
...
```

Dependency
----------

Disclaimer:
This is maybe a incomplete list. Please notice that some dependency libraries may **require** a **reproduction** of copyright and license, **even if they are shipped as binary!!**

* **Arduino.h**

  * From: Arduino IDE / target specific
  * License: (target: Arduino) GNU Lesser General Public License 2.1
  
* **SPI.h**

  * From: Arduino IDE / target specific
  * License: (target: Arduino) GNU Lesser General Public License 2.1
  
* **stdint.h**

  * From: Arduino IDE / Compiler and target specific
  * License: different

* **stdio.h**

  * From: Arduino IDE / Compiler and target specific
  * License: different
  
* **stdlib.h**

  * From: Arduino IDE / Compiler and target specific
  * License: different
  
* **string.h**

  * From: Arduino IDE / Compiler and target specific
  * License: different

License
-------
Apache License 2.0 (see [LICENSE.md](https://github.com/thotro/arduino-dw1000/blob/master/LICENSE.md))

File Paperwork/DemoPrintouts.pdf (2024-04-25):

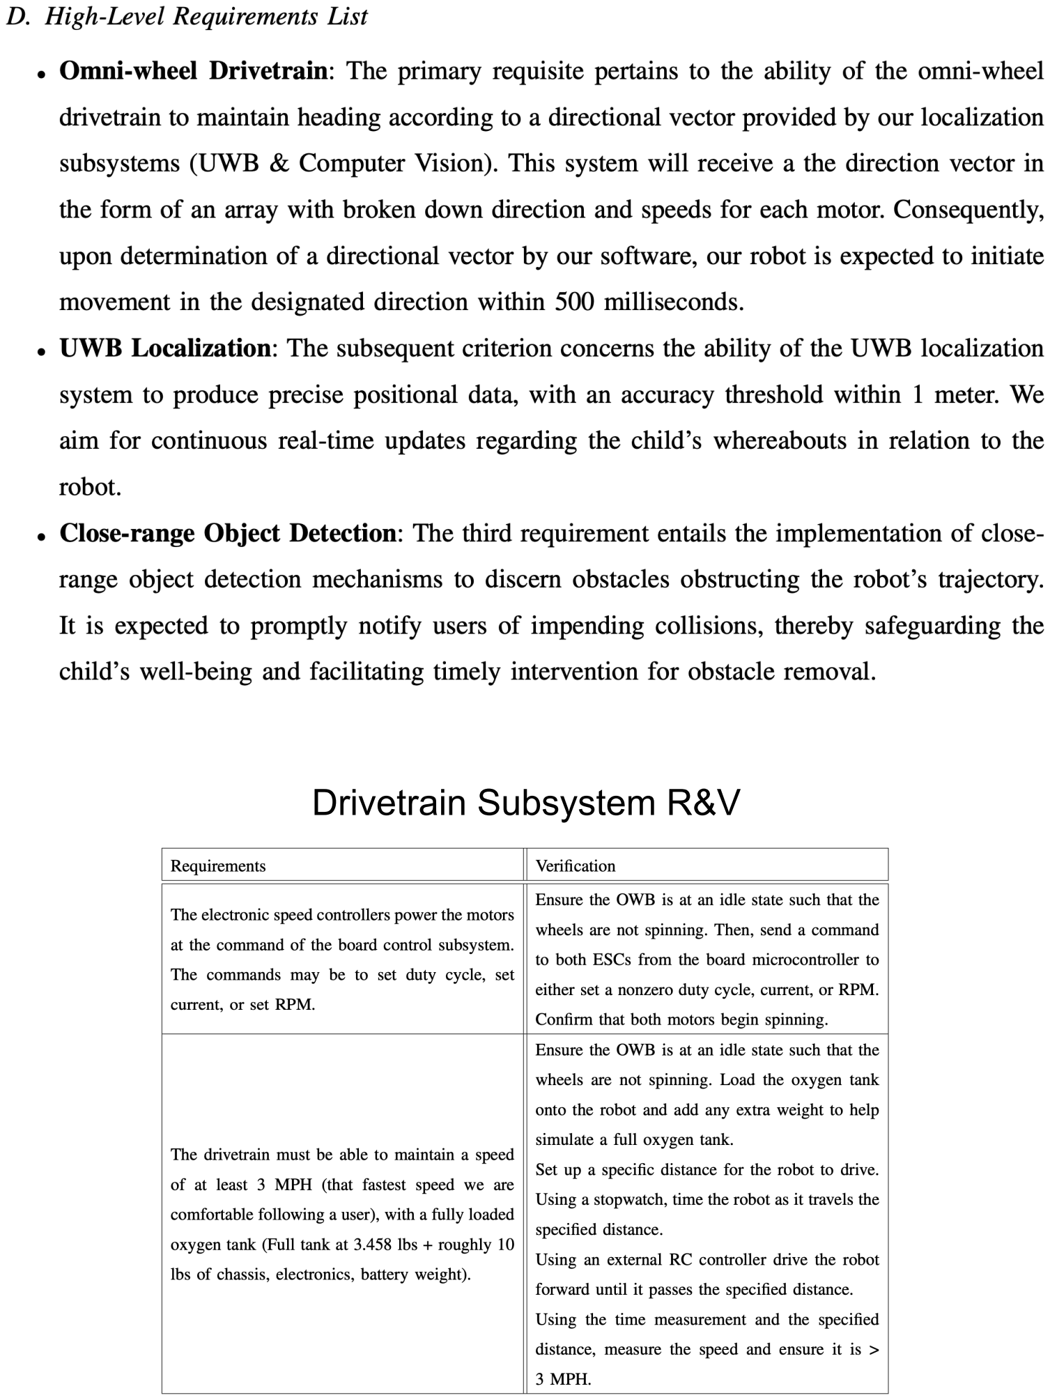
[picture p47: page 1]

Drivetrain Subsystem R&V

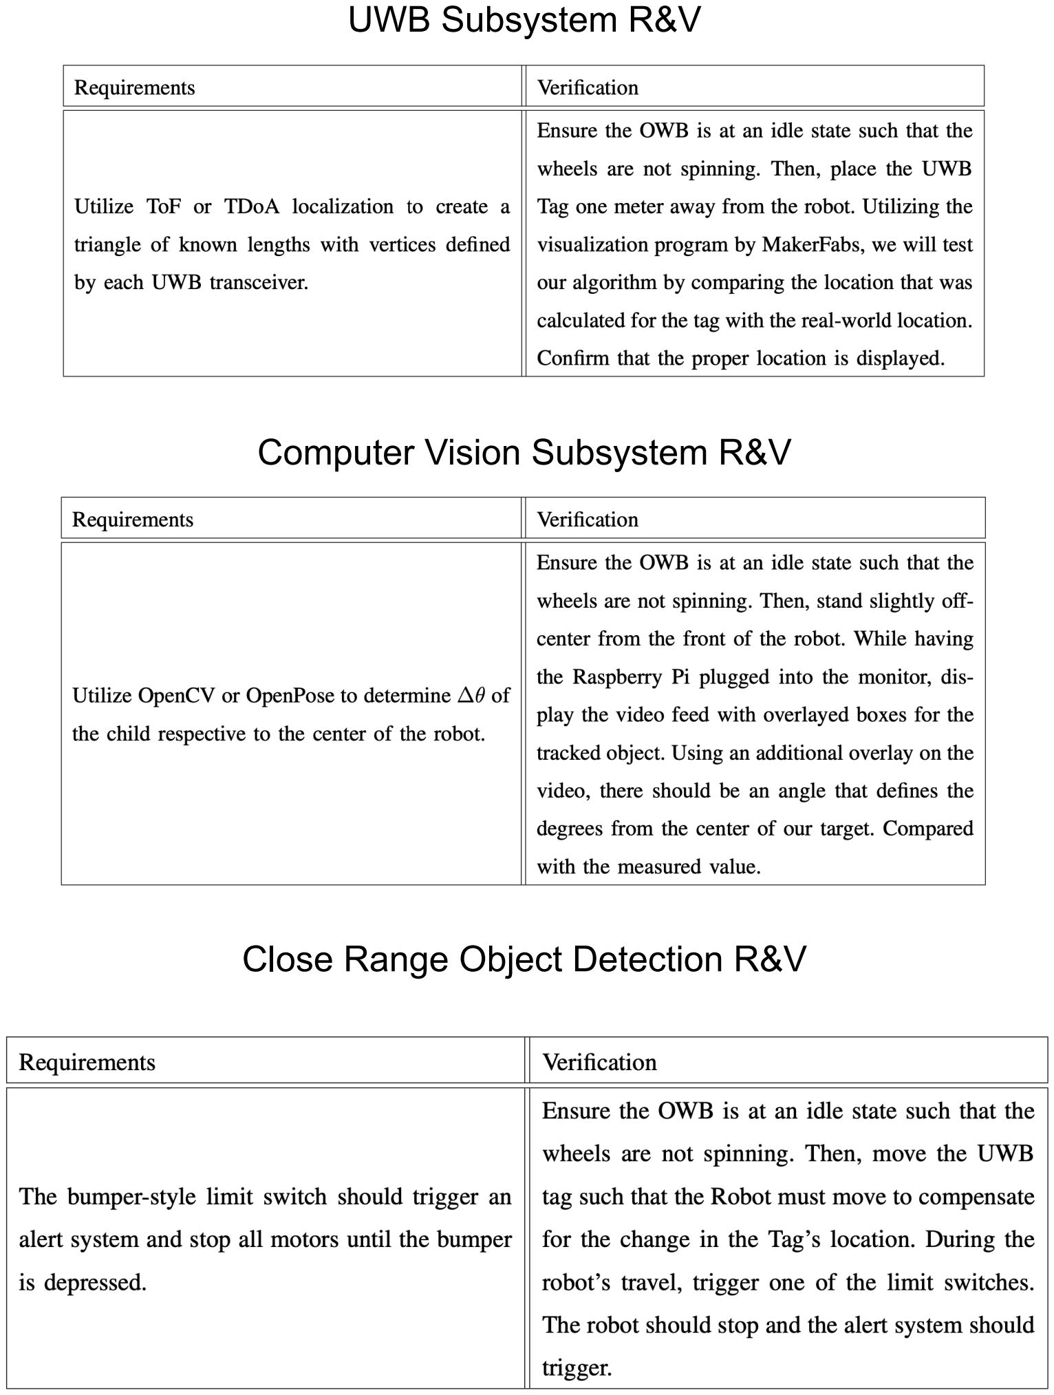
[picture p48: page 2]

UWB Subsystem R&V

Computer Vision Subsystem R&V

Close Range Object Detection R&V

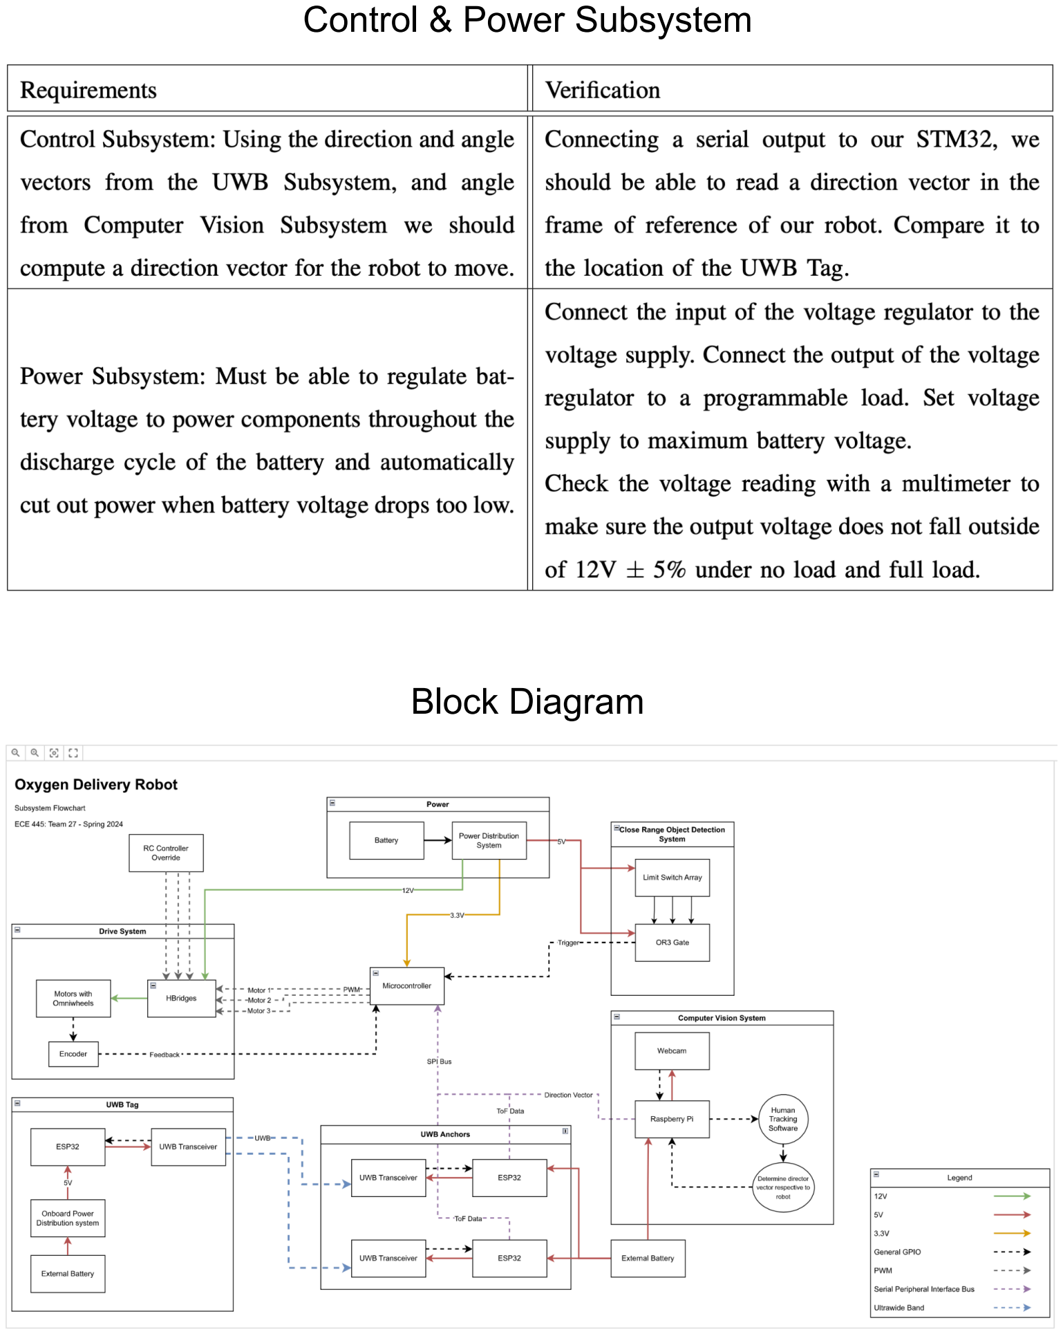
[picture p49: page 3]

Control & Power Subsystem

Block Diagram

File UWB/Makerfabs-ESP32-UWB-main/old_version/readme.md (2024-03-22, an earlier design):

# Makerfabs ESP32 UWB

```c++
/*
Version:		V3.0
Author:			Vincent
Create Date:	2021/11/6
Note:
	2021/12/9 	V2.0:Add a Indoor Positioning demo.
	2022/6/29 	V2.1:Add DW3000 library.
	2022/8/1  	V3.0:Provides a library available for high-power versions. Move DW3000 to other 		  					     repositories.
	2022/9/6	V3.1:Added changes to the high-power version.

*/
```


[toc]

# Makerfabs

[Makerfabs home page](https://www.makerfabs.com/)

[Makerfabs Wiki](https://makerfabs.com/wiki/index.php?title=Main_Page)

# Makerfabs ESP32 UWB
## Intruduce

Product Link ：[esp32-uwb-ultra-wideband](https://www.makerfabs.com/esp32-uwb-ultra-wideband.html) 

Wiki Link : [ESP32_UWB](https://www.makerfabs.com/wiki/index.php?title=ESP32_UWB) 

Makerfabs ESP32 UWB contains an ESP32 and a DW1000 chip.

The DW1000 is a single-chip wireless transceiver based on ultra-wideband technology. The chip enables you to develop cost-effective RTLS solutions that can pinpoint indoor and outdoor positioning to within 10 cm.

The chip provides a new approach to real-time location and indoor location systems, location-based services, wireless sensor networks and the Internet of Things by providing accurate location awareness and communication.

UWB - X1 - PRO module is our decaWave DW1000 chip design company based UWB transceiver module products. After the encapsulation All compatible DWM1000, pin pin to pin, can directly replace to use. The antenna is integrated in the module and all of the rf circuit, power management and clock circuit is equal to one.

Based on our actual tests, the range range of the standard DW1000 is around 47 meters, and the long-distance version can reach 125 meters. Of course, it depends on the test environment.

## Feature

- Integrated ESP32 2.4G WiFi and Bluetooth.
- DW1000 UWB module.
- UWB - X1 - PRO module.(Long range)

### Front:

front

### Back:
back

### Long Range Version UWB-X1-Pro

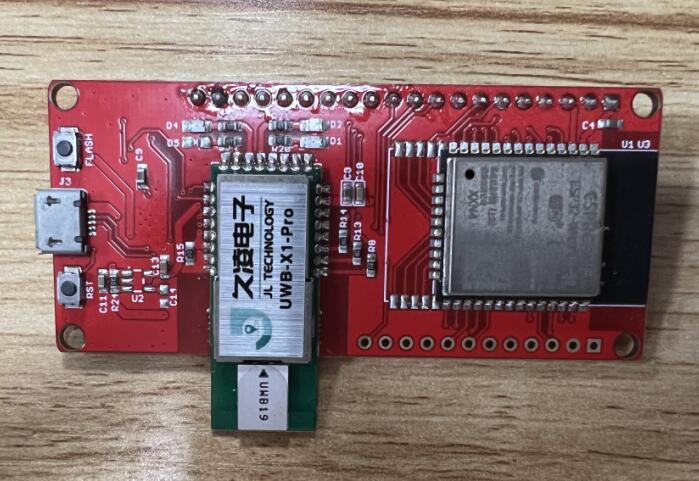
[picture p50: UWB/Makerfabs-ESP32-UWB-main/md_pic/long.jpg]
long


# Example

## Equipment list

- At least two ESP32 UWB

## Compiler Options

**If you have any questions，such as how to install the development board, how to download the code, how to install the library. Please refer to :[Makerfabs_FAQ](https://github.com/Makerfabs/Makerfabs_FAQ)**

- Install board : ESP32 .
- Install library : arduino-dw1000
- Change code in DW1000.cpp

```c++
void DW1000Class::begin(uint8_t irq, uint8_t rst) {
	// generous initial init/wake-up-idle delay
	delay(5);
	// Configure the IRQ pin as INPUT. Required for correct interrupt setting for ESP8266
    	pinMode(irq, INPUT);
	// start SPI
	SPI.begin();

// Change By VINCENT
// #ifndef ESP8266
// 	SPI.usingInterrupt(digitalPinToInterrupt(irq)); // not every board support this, e.g. ESP8266
// #endif

	// pin and basic member setup
	_rst        = rst;
	_irq        = irq;
	_deviceMode = IDLE_MODE;
	// attach interrupt
	//attachInterrupt(_irq, DW1000Class::handleInterrupt, CHANGE); // todo interrupt for ESP8266
	// TODO throw error if pin is not a interrupt pin
	attachInterrupt(digitalPinToInterrupt(_irq), DW1000Class::handleInterrupt, RISING); // todo interrupt for ESP8266
}
```

Comment out these code, or a compilation error will occur.

```c++
// #ifndef ESP8266
// 	SPI.usingInterrupt(digitalPinToInterrupt(irq)); // not every board support this, e.g. ESP8266
// #endif
```

- Upload code, select board "ESP32 DEV"

**V3.0 Update**

Modify by [DW1000](https://github.com/thotro/arduino-dw1000) version 0.9.0

Provides a library available for high-power versions. It is also compatible with the standard DW1000, and in fact only adds an initialization function for the high-power version. Of course, it also includes the changes above.

```c++

// Vincent changes
// For large power moudle
void DW1000Class::large_power_init()
{
	// uint32 reg;
	// reg = dwt_read32bitreg(GPIO_CTRL_ID);
	// reg |= 0x00014000;
	// reg |= 0x00050000;
	// dwt_write32bitreg(GPIO_CTRL_ID, reg);
	// dwt_write16bitoffsetreg(PMSC_ID, PMSC_TXFINESEQ_OFFSET, PMSC_TXFINESEQ_DISABLE);

	byte reg[4];

	readBytes(GPIO_CTRL, 0, reg, 4);

	reg[1] |= 0x40;
	reg[2] |= 0x01;
	reg[2] |= 0x05;

	writeBytes(GPIO_CTRL, 0, reg, 4);

	reg[0] = reg[1] = reg[2] = reg[3] = 0;
	writeBytes(PMSC, 0x26, reg, 2);

	reg[0] = 0xC0;
	reg[1] = 0;
	reg[2] = 0;
	reg[3] = 0;
	writeBytes(TX_CAL, TC_PGDELAY_SUB, reg, 1);

	reg[0] = 0x1f;
	reg[1] = 0x1f;
	reg[2] = 0x1f;
	reg[3] = 0x1f;
	writeBytes(TX_POWER, 0, reg, 4);
}
```

**V3.1 Update**

By changing the channel from Channel5 to Channel2, the distance of UWB-X1-Pro can reach 320M.

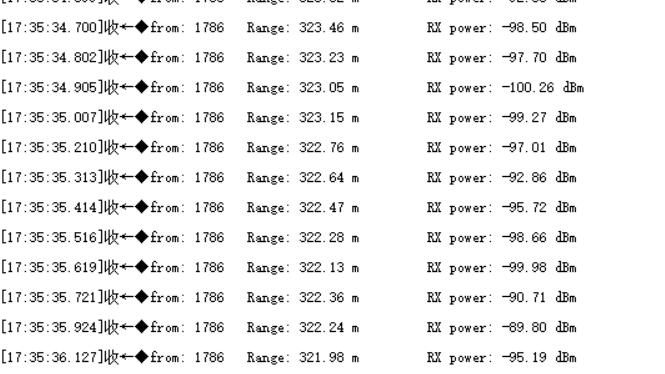
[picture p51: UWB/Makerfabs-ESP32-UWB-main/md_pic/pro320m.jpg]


This is due to the fact that the X1-Pro's antenna is optimized for Channel2.

But Makerfabs could not provide further technical support, just suggestions from suppliers.

If you're interested, try DW1000_channel2.zip, or make changes directly in the DW1000 library code.

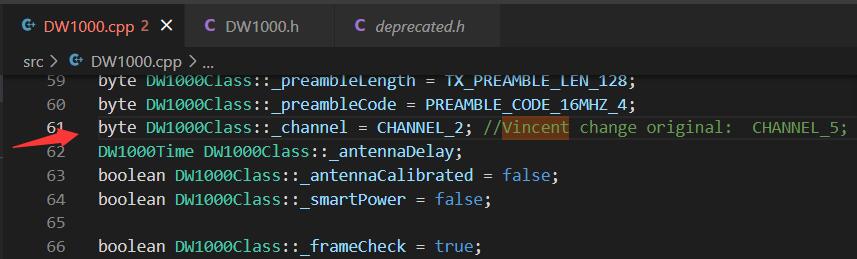
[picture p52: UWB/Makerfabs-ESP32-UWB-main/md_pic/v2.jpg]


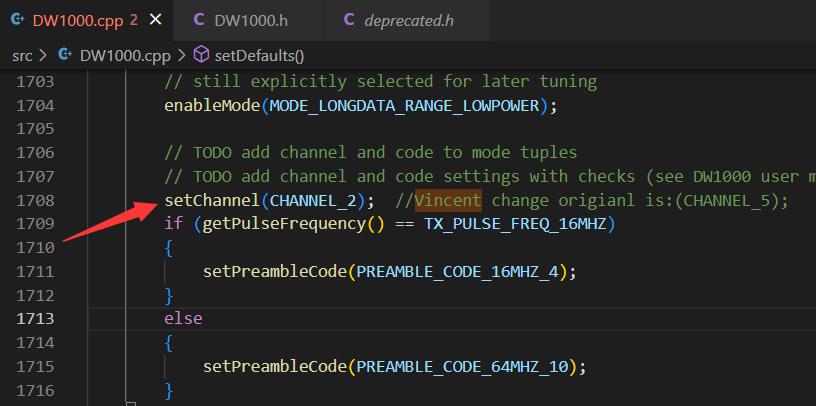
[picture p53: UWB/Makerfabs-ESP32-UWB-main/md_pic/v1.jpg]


## Example List

### Anchor

Distance test anchor point.

### Tag

Distance to the receiving end of the test. You need an anchor point to receive data.

### Tag_1306

There is an SSD1306 screen receiver, and a data structure for storing multiple anchor points is implemented. (The screen can display a maximum of two anchors, you can modify the font size to show more anchors). You need an anchor point to receive data.

### Indoor positioning

Three UWB modules were used for indoor plane positioning. Data is transmitted through UDP protocol and graphically displayed in Python. 



The law of cosines is used to calculate tag coordinates.

```python
def tag_pos(a, b, c):
    # p = (a + b + c) / 2.0
    # s = cmath.sqrt(p * (p - a) * (p - b) * (p - c))
    # y = 2.0 * s / c
    # x = cmath.sqrt(b * b - y * y)
    cos_a = (b * b + c*c - a * a) / (2 * b * c)
    x = b * cos_a
    y = b * cmath.sqrt(1 - cos_a * cos_a)

    return round(x.real, 1), round(y.real, 1)
```

## Code Explain

- Define Pins

```c++
#define SPI_SCK 18
#define SPI_MISO 19
#define SPI_MOSI 23
#define DW_CS 4

// connection pins
const uint8_t PIN_RST = 27; // reset pin
const uint8_t PIN_IRQ = 34; // irq pin
const uint8_t PIN_SS = 4;   // spi select pin
```

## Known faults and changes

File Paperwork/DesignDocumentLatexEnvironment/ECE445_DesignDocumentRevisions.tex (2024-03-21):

\documentclass[journal,onecolumn, draftclsnofoot, 12pt]{IEEEtran}
\usepackage[margin=1in]{geometry}
\usepackage[utf8]{inputenc}
\usepackage{graphicx}
\usepackage{times}
\usepackage{algorithm}
\usepackage{algpseudocode}
\usepackage{graphicx}
\usepackage{amsmath}
\usepackage{subcaption}
\usepackage{amsmath,amsfonts,amssymb,amsthm,commath,dsfont,enumitem}
\usepackage[colorlinks,urlcolor=blue,citecolor=blue]{hyperref}
\usepackage{xcolor}
\usepackage{listings}
\usepackage{todonotes}
\usepackage[T1]{fontenc}
\usepackage{graphicx} % for including the logo
\usepackage{fancyhdr} % for customizing the footer
\usepackage{tikz} % for the flowchart
\usetikzlibrary{shapes.geometric} % for tikz charts
\usetikzlibrary {arrows.meta,bending,positioning} % for tikz charts
\usepackage{array} % for R&V Tables
\usepackage{hyperref} % for hyper links

\pagestyle{fancy}

% % Define a new command to include a logo
% \newcommand{\logo}{\includegraphics[width=1.0cm]{OWB_cutout.png}}

% % Customize the footer to include the logo on the bottom right of pages 3 to 5
% \fancyfoot[LO,RE]{\ifnum\value{page}>3\ifnum\value{page}<19\logo\fi\fi}

% Setting color formatting for Python code
\lstset{
    language=Python,
    basicstyle=\fontsize{8}{10}\ttfamily,
    keywordstyle=\color{blue},
    stringstyle=\color{red},
    commentstyle=\color{green},
    morecomment=[l][\color{magenta}]{\#},
}

% Setting color formatting for C code
\lstset{
    language=C,
    basicstyle=\fontsize{8}{10}\ttfamily,
    keywordstyle=\color{blue},
    stringstyle=\color{red},
    commentstyle=\color{green!50!black},
    morecomment=[l][\color{magenta}]{\#},
    frame=tb,
    numbers=left,
    numberstyle=\tiny\color{gray},
    breaklines=true,
    showstringspaces=false,
}

% macros adapted from matus & djhsu
\def\ddefloop#1{\ifx\ddefloop#1\else\ddef{#1}\expandafter\ddefloop\fi}
\def\ddef#1{\expandafter\def\csname bb#1\endcsname{\ensuremath{\mathbb{#1}}}}
\ddefloop ABCDEFGHIJKLMNOPQRSTUVWXYZ\ddefloop
\def\ddef#1{\expandafter\def\csname b#1\endcsname{\ensuremath{\mathbf{#1}}}}
\ddefloop ABCDEFGHIJKLMNOPQRSTUVWXYZ\ddefloop
\def\ddef#1{\expandafter\def\csname c#1\endcsname{\ensuremath{\mathcal{#1}}}}
\ddefloop ABCDEFGHIJKLMNOPQRSTUVWXYZ\ddefloop

\DeclareMathOperator*{\argmin}{arg\,min}
\DeclareMathOperator*{\argmax}{arg\,max}
\DeclareMathOperator*{\softmax}{softmax}

\newenvironment{Q}{\item}{\phantom{s}}
\newenvironment{Solution}{\color{blue}\begin{enumerate}}{\end{enumerate}}

\begin{document}
\maketitle

\begin{titlepage}
    \begin{center}
        \vspace*{1cm}
            
        \Huge
        \textbf{ECE 445 Design Document - Spring 2024}
            
        \vspace{0.5cm}
        \LARGE
        OXYGEN DELIVERY ROBOT
            
        \vspace{1.5cm}

        \large
        Team \#27 \\
        Rutvik Sayankar \\ Aidan Dunican \\ Nazar Kalyniouk \\

        \vspace{1cm}
        
        TA: Selva Subramaniam

        \vspace{1.5cm}
            
        \vfill

        \vspace{0.8cm}
            
        \Large
        February 22nd, 2024 \\
        ECE 445: Senior Design Project Lab \\
        University of Illinois at Urbana-Champaign\\
            
    \end{center}
\end{titlepage}

\pagebreak

\tableofcontents

\pagebreak

\section{Terms and Keywords}
\vspace{0.8cm}
\begin{itemize}
    \item ChILD - Children's Interstitial and Diffuse Lung Disease
    \item PCB – Printed Circuit Board
    \item OWB - Three-Wheeled Omni-Wheel Bot
    \item UWB - Ultra-wideband is a radio technology that can use a very low energy level for short-range, high-bandwidth communications over a large portion of the radio spectrum.
    \item ESP32 - A series of low-cost, low-power system-on-a-chip microcontrollers with integrated Wi-Fi and dual-mode Bluetooth.
    \item RPM - Revolutions per minute
    \item GPIO - General-purpose input/output
    \item PWM - Pulse-width modulation
    \item MPH - Miles per hour
    \item OpenCV - (Open Source Computer Vision Library) is an open source computer vision and machine learning software library.
    \item OpenPose - Real-time multi-person keypoint detection library for body, face, hands, and foot estimation.
    \item TDoA - Time Difference of Arrival 
    \item ToF - Time of Flight
\end{itemize}

\pagebreak

\section{Introduction}

\subsection{Problem}
Children's interstitial and diffuse lung disease (ChILD) is a collection of diseases or disorders. These diseases cause a thickening of the interstitium (the tissue that extends throughout the lungs) due to scarring, inflammation, or fluid buildup \cite{ChILD-2022}. This eventually affects a patient’s ability to breathe and distribute enough oxygen to the blood.

Numerous children experience the impact of this situation, requiring supplemental oxygen for their daily activities. It hampers the mobility and freedom of young infants, diminishing their growth and confidence. Moreover, parents face an increased burden, not only caring for their child but also having to be directly involved in managing the oxygen tank as their child moves around.

\subsection{Solution}
Given the absence of relevant solutions in the current market, our project aims to ease the challenges faced by parents and provide the freedom for young children to explore their surroundings. As a proof of concept for an affordable solution, we propose a three-wheeled omnidirectional mobile robot capable of supporting filled oxygen tanks in the size range of M-2 to M-9, weighing 2.2 - 13.2 lbs (1 - 6kg) respectively (when full). Due to time constraints in the class and the objective to demonstrate the feasibility of a low-cost device, we plan to construct the robot at a roughly 50 percent scale of the proposed solution. Consequently, our robot will handle simulated weights/tanks with weights ranging from 1.1 - 6.6 lbs (0.5 - 3 kg). For our prototyping and testing, we will be utilizing an empty M-6 oxygen tank (height = 15", diameter = 3.2", empty weight = 2.8 lbs/1.27kg, capacity = 165L \cite{oxygen_tank_sizes}).

As mentioned the robot will have a three-wheeled omni-wheel drive train, incorporating two localization subsystems to ensure redundancy and enhance child safety. The first subsystem utilizes ultra-wide band (UWB) transceivers for triangulating the child's location relative to the robot in indoor environments, this is similar to how Apple AirTags triangulate their location relative to an iPhone \cite{airtag_uwb} (although AirTags use a combination of UWB and Bluetooth triangulation \cite{airtag_ble}). The second subsystem makes use of a desktop web camera which streams video to a Raspberry Pi where it will leverage open-source object tracking libraries to improve our directional accuracy in tracking a child. The final main subsystem focuses on the drive train and chassis of the robot.

As part of the design, we intend to create a PCB in the form of a Raspberry Pi hat, facilitating convenient access to information generated by our computer vision system, and saving space on our robot. The PCB will incorporate all motor control components, limit switch connections, GPIO pass through for the Raspberry Pi, power distribution and step down converter, and an STM32 based microcontroller serving as the project's central processing unit. This microcontroller will control the drivetrain, analyze UWB localization data, and use the direction vector provided by the computer vision system to calculate the speed and direction of each wheel.

\subsection{Visual Aid}

\begin{figure}[H]
\begin{center}
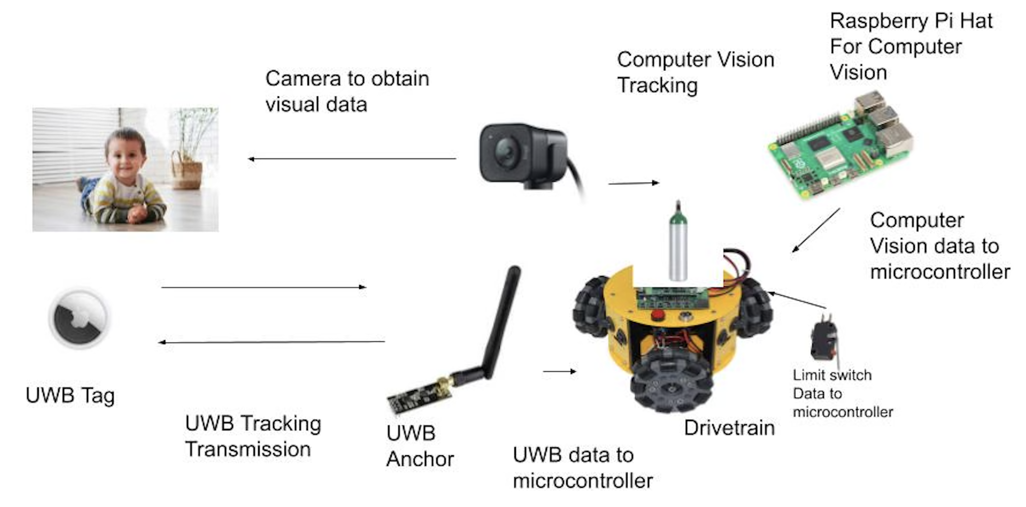
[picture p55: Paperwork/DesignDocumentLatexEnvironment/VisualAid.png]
\\
\caption{ Visual aid for our project.  } 
\label{fig:visualaid}
\end{center}
\end{figure}

\newpage

\subsection{High-Level Requirements List}
\begin{itemize}
    \item \textbf{Omni-wheel Drivetrain}: 
    The primary requisite pertains to the ability of the omni-wheel drivetrain to maintain heading according to a directional vector provided by our localization subsystems (UWB \& Computer Vision). This system will receive a the direction vector in the form of an array with broken down direction and speeds for each motor. Consequently, upon determination of a directional vector by our software, our robot is expected to initiate movement in the designated direction within 500 milliseconds.

    \item \textbf{UWB Localization}: 
    The subsequent criterion concerns the ability of the UWB localization system to produce precise positional data, with an accuracy threshold within 1 meter. We aim for continuous real-time updates regarding the child's whereabouts in relation to the robot.
    
    \item \textbf{Close-range Object Detection}: 
    The third requirement entails the implementation of close-range object detection mechanisms to discern obstacles obstructing the robot's trajectory. It is expected to promptly notify users of impending collisions, thereby safeguarding the child's well-being and facilitating timely intervention for obstacle removal.
    
\end{itemize}

\newpage

\section{Design}
\subsection{Block Diagrams}

\begin{figure}[H]
\begin{center}
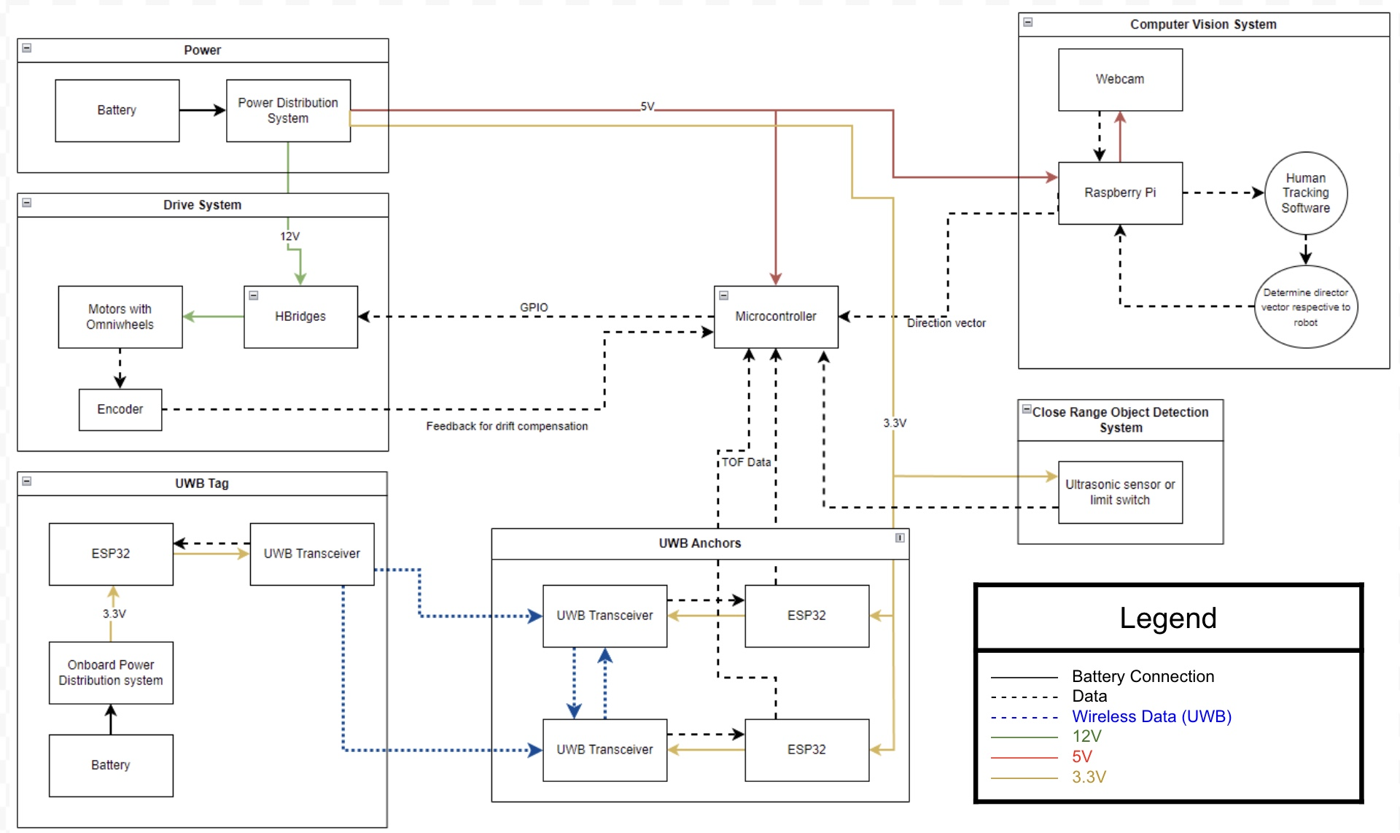
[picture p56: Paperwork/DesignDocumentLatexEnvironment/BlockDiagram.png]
\\
\caption{High-level block diagram for our project.  } 
\label{fig:blockdiagram}
\end{center}
\end{figure}

\subsection{Subsystems Overview}
\begin{itemize}
    \item \textbf{Drivetrain Subsystem}: The Drivetrain subsystem will encompass the motors, omni-wheels, encoder, and electronic speed controllers. It will receive instructions from the Control subsystem to control the motors and feed encoder data for drift compensation back to the Control subsystem (three-wheeled omni-wheel bots are easily affected by drift if it is not compensated for).
    \item \textbf{UWB Subsystem}: This subsystem contains tag and anchor components. The UWB tag will consist of the UWB transceiver, battery, ESP32, and onboard power distribution system. It will attach to the child that is being tracked (through velcro or some similar method). The UWB signals emitted are received by the UWB anchors. It will work with the UWB anchors subsystem to determine the location of the tag relative to the robot. The UWB anchors will consist of the UWB transceivers and ESP32s. This subsystem communicates with the Control Subsystem to relay a distance and angle that corresponds to the position of the tag relative to the anchors. Both of these systems will utilize transceiver boards based on Decawave DW3000 ICs \cite{9881375}.
    \item \textbf{Computer Vision Subsystem}: This subsystem will include a web camera connected to a Raspberry Pi. Implementing an image-processing algorithm using OpenCV or OpenPose it will analyze data from the web camera to locate the child. It will connect to the microprocessor and provide an angle. This angle will correspond to the change in angle required by the robot to keep the child within the center of the image frame (this will correspond to directly in front of the robot).
    \item \textbf{Close-Range Object Detection System}: This subsystem, consisting of bumper-style limit switches will communicate with the Control Subsystem to provide information about nearby obstacles. When an obstacle is detected (i.e. a limit switch has been activated), the user will be alerted to adjust the robot's path or clear the obstacle (through an LED or simple speaker). This feature will ensure effective obstacle avoidance and will enhance the safety of the robot.
    \item \textbf{Control and Power Subsystem}: The Control Subsystem will be responsible for taking in the distance and angle from the UWB Subsystem and the angle from the Computer Vision Subsystem. Facilitating a sensor fusion with this data, it will compute a velocity vector that the robot must move to remain within $\sim 1$ meter of the child. Using the kinematics detailed in section \ref{sec:OWBKinematics}, the velocity vector will be decomposed into its components to obtain the motor speed and direction for each omnidirectional wheel. 
    
    The Power Subsystem is responsible for supplying power to all other components of the robot. It will include a 12V battery and power distribution system. This subsystem will supply 12V power to the drive system. It will supply 5V to our STM32-based microcontroller, computer vision subsystem, and motor encoders. Lastly, it will supply 3.3V to the close-range object detection system and the UWB anchors.
\end{itemize}

\newpage

\subsection{Physical Design}
A rough idea of how everything will be put onto our robot is shown in figure \ref{fig:PhysicalDesign}.

\begin{figure}[H]
\begin{center}
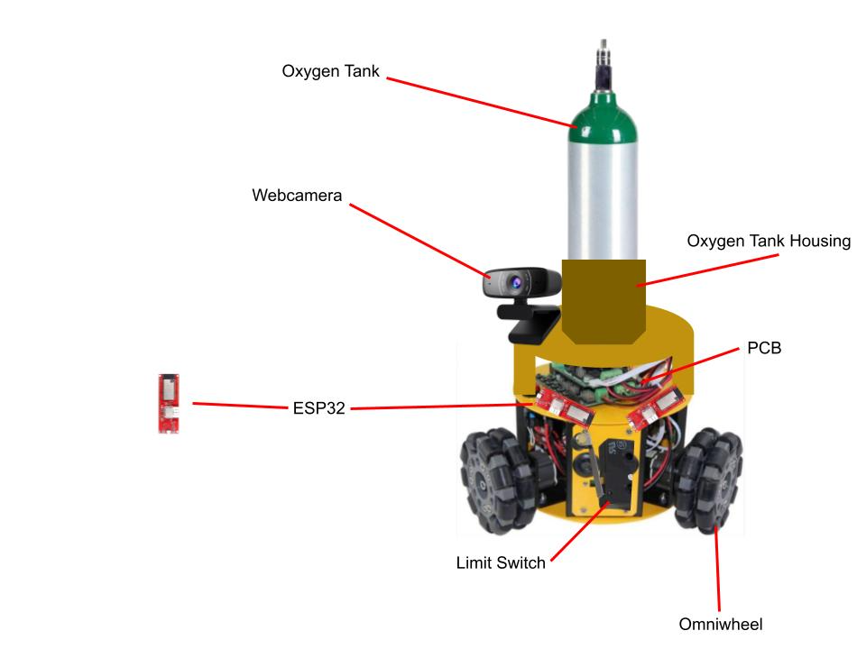
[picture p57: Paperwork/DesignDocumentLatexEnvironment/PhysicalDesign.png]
    \\
    \caption{ Physical Layout  } 
    \label{fig:PhysicalDesign}
\end{center}
\end{figure}

\subsection{Drivetrain Subsystem}
This subsystem encapsulates everything required to move the chassis of the robot. To facilitate testing we will be using a RC Transmitter Controller which is detailed in section \ref{sec:RCController}. For more information regarding our choices of the commercial components that make up the Drivetrain Subsystem, please refer to section \ref{sec:cost}. Regarding the safety of our OWB, the Drivetrain Subsystem must accept commands from the Control Subsystem to set the relative speed of the motors.

\subsubsection{Kinematics of the OWB}
\label{sec:OWBKinematics}
In a three-wheeled omni-wheel robot, the three wheels are arranged in a triangular pattern, with one wheel at the front and two wheels at the back. Each wheel has several small omnidirectional wheels arranged in a circular pattern, which allows the robot to move in any direction.

To move the robot, each wheel is driven independently using a motor. By varying the speed and direction of each wheel, the robot can move in any direction and rotate around its center point.

The kinematics of a three-wheeled omni-wheel robot can be modeled mathematically through the below equations \cite{riky2021omnidirectional} which relate the robot's linear and angular velocities to the speed and direction of each wheel.

We first define for each wheel a direction of rotation $V_i$, and the resulting movement effected in the x and y axes, $V_ix$ and $V_iy$ as shown below.

\begin{figure}[H]
  \centering
  \begin{minipage}[b]{0.45\linewidth}
    \centering
    
    \caption{Vector Definitions}
    \label{fig:vecdef}
  \end{minipage}
  \hfill
  \begin{minipage}[b]{0.45\linewidth}
    \centering
    
    \caption{OWB drive vectors \cite{wada2015OWB}}
    \label{fig:owb_vec}
  \end{minipage}

  \label{fig:vecs}
\end{figure}

Knowing the angle of each wheel from the vertical axis, we can compute the x and y components created by the rotation of each wheel. By summing these components together, we can get the effective motion of the robot in the x, y and yaw axes.

\[
\begin{pmatrix}
V_x \\
V_y \\
\omega
\end{pmatrix}
=
\begin{pmatrix}
1 & - \frac{1}{2} & -\frac{1}{2} \\
0 & -\frac{\sqrt{3}}{2} & \frac{\sqrt{3}}{2} \\
1 & 1 & 1
\end{pmatrix}
\begin{pmatrix}
V_1 \\
V_2 \\
V_3
\end{pmatrix}
\]
    
$V_{x}$ and $V_{y}$ are the desired linear velocities in the x and y directions, respectively, and omega is the desired angular velocity. $V_{1}$, $V_{2}$, and $V_{3}$ are the velocities of the three wheels, and L is the distance between the robot's center of mass and the wheel axes.

\[
\begin{pmatrix}
V_1 \\
V_2 \\
V_3
\end{pmatrix}
=
\begin{pmatrix}
1 & - \frac{1}{2} & -\frac{1}{2} \\
0 & -\frac{\sqrt{3}}{2} & \frac{\sqrt{3}}{2} \\
1 & 1 & 1
\end{pmatrix}^{-1}
\begin{pmatrix}
V_x \\
V_y \\
\omega
\end{pmatrix}
\]

By taking the inverse of our 3x3 component coefficient matrix above, we can solve for our individual motor speeds $V_1$, $V_2$ and $V_3$, given the desired motion in terms of $V_x$, $V_y$, and $w$.

\subsubsection{Communication for RC Controller}
\label{sec:RCController}
For our RC controller, we plan to use a Flysky FS-i6 6CH 2.4GHz Radio System RC Transmitter Controller with FS-iA6 Receiver. 

This controller communicates with its receiver, the FS-iA6, using a 2.4 GHz digital frequency-hopping spread spectrum (FHSS) communication protocol.

In FHSS, the transmitter and receiver periodically hop between different channels within the 2.4 GHz frequency band to avoid interference from other devices operating on the same frequency band. The specific channels used are selected automatically by the transmitter and receiver and can be different for each transmission.

The FS-i6 transmitter sends digital signals to the FS-iA6 receiver, which is connected to the RC vehicle's onboard electronics. The transmitter and receiver are bound together before use, which pairs them and allows them to communicate securely.

The FS-i6 transmitter has six channels of control, which means it can transmit six different control signals to the receiver at the same time. These channels can be used to control the movement of the RC vehicle's motors and servos, as well as to operate other electronic components such as lights or sound systems.

For our operations, we plan to use three channels, using our OWB as our frame of reference, we used one channel for linear control in the $x-axis$ a second for linear control in the $y-axis$, and a third channel for rotational control $w$

The OWB can move forward and backward like a normal RC car. This motion is represented by $V_y$, and is mapped to CH1 on the transmitter (refer to figure \ref{fig:ChannelDistribution} for detail on channel mapping). While a normal RC car needs a $V_y$ component to turn left or right, the OWB can "yaw" on the spot. This is represented by $w$, and is mapped to CH3 on the transmitter. The final unique motion the OWB can execute is a "drift" toward the left or right. This motion is represented by $V_x$ and is mapped to CH2 on the transmitter.

Thus, using these three channels, we can define the robot's desired $V_x$, $V_y$, and $w$. These desired motion vectors are then fed to our inverse kinematics algorithm, which breaks down our desired motion into an individual wheel speed and direction for each motor.

\begin{figure}[H]
\begin{center}
    \\
    \caption{ Channel Distribution  } 
    \label{fig:ChannelDistribution}
\end{center}
\end{figure}

\newpage

\subsubsection{Requirements and Verification}
\begin{center}
\begin{tabular}{ | m{20em} || m{20em} | } 
  \hline
  Requirements & Verification  \\ 
  \hline
  \hline
  The electronic speed controllers power the motors at the command of the board control subsystem. The commands may be to set duty cycle, set current, or set RPM. 
  & 
  Ensure the OWB is at an idle state such that the wheels are not spinning. Then, send a command to both ESCs from the board microcontroller to either set a nonzero duty cycle, current, or RPM. Confirm that both motors begin spinning.
  \\ 
  \hline
  The drivetrain must be able to maintain a speed of at least 3 MPH (that fastest speed we are comfortable following a user), with a fully loaded oxygen tank (Full tank at 3.458 lbs + roughly 10 lbs of chassis, electronics, battery weight).
  & 
  Ensure the OWB is at an idle state such that the wheels are not spinning. Load the oxygen tank onto the robot and add any extra weight to help simulate a full oxygen tank. 
  
  Set up a specific distance for the robot to drive. Using a stopwatch, time the robot as it travels the specified distance.
  
  Using an external RC controller drive the robot forward until it passes the specified distance.
  
  Using the time measurement and the specified distance, measure the speed and ensure it is > 3 MPH.
  \\
  \hline
\end{tabular}
\end{center}

\vspace{0.8cm}

\subsection{UWB Subsystem}
This subsystem encapsulates everything required to obtain a direction and angle of the UWB Tag relative to the UWB Anchors. It will transmit these values to the Control Subsystem. To facilitate the testing of our localization algorithm we will use the indoor positioning visualization example provided by MakerFabs (\url{https://github.com/Makerfabs/Makerfabs-ESP32-UWB.git}). There are two steps to our localization algorithm that are detailed in section \ref{sec:Localization}. For more information regarding our choices of the commercial components that make up the UWB Subsystem, please refer to section \ref{sec:cost}.

\vspace{0.5cm}

\subsubsection{Localization Algorithms}
\label{sec:Localization}

There are two main localization techniques when we use UWB, Time Difference of Arrival (TDoA) and Time of Flight (ToF) \cite{localization}.

ToF is a positioning method based on two-way ranging. That means the tag needs to send and receive signals from the anchor several times and then the flight time of the signal between the anchor and the tag can be measured, because radio waves travel at the speed of light, we can calculate the distance between the tag and each anchor.

TDoA is localization based on comparing the time difference between signals and each anchor and this technique requires an accurate time synchronization function. When using the TDoA method, the UWB tag will send out a poll message, and all the nearby UWB anchors will receive it and record the arrival time. Because the location of anchors is different, they won’t receive the message at the same time. We can use these time differences to determine the tag’s location.

This algorithm will essentially provide us with the sides of a triangle, with which we can calculate the location of the tag, we will be using the law of cosines to triangulate the location of the tag relative to the anchors.

\begin{algorithm}[H]
    \SetAlgoLined
    
    \Input{\textbf{Input}: Lengths of sides $(a, b, c)$}\\
    \Output{\textbf{Output}: Coordinates $(x, y)$} 

    % cos_a = (b * b + c*c - a * a) / (2 * b * c)
    % x = b * cos_a
    % y = b * cmath.sqrt(1 - cos_a * cos_a)
    
    $ \text{cos\_a} = \frac{{b^2 + c^2 - a^2}}{{2bc}} $\; \\
    $ x = b \cdot \text{cos\_a} $\; \\
    $ y = b \cdot \sqrt{1 - \text{cos\_a}^2} $\; \\
    
    \Return{$ (\text{round}(x.\text{real}, 1), \text{round}(y.\text{real}, 1)) $}\;
    
    \caption{Calculation of Coordinates using Law of Cosines}
\end{algorithm}

\newpage

\subsubsection{Requirements and Verification}
\begin{center}
\begin{tabular}{ | m{20em} || m{20em} | } 
  \hline
  Requirements & Verification  \\ 
  \hline
  \hline
  Utilize ToF or TDoA localization to create a triangle of known lengths with vertices defined by each UWB transceiver.
  & 
  Ensure the OWB is at an idle state such that the wheels are not spinning. Then, place the UWB Tag one meter away from the robot. Utilizing the visualization program by MakerFabs, we will test our algorithm by comparing the location that was calculated for the tag with the real-world location. Confirm that the proper location is displayed.
  \\ 
  \hline
\end{tabular}
\end{center}

\subsection{Computer Vision Subsystem}
This subsystem encapsulates everything required to obtain the angle of the child relative to the OWB. It will transmit this value to the Control Subsystem. To facilitate the testing of this subsystem we will connect our Raspberry Pi to monitor in order to ensure that we are properly locating and tracking the child. For more information regarding our choices of the commercial components that make up the Computer Vision Subsystem, please refer to section \ref{sec:cost}.

\vspace{0.5cm}

\subsubsection{OpenCV Algorithms}
The code will load a pre-trained Haar cascade classifier specifically designed for detecting full-body patterns, which will assist in identifying individuals within images.
 
When a child is detected within the image, the algorithm analyzes their position. This involves calculating the center point of the detected child's body and determining the relative distance between this center point and the center of the entire image.
 
The algorithm calculates center points and the relative distance. A variable called "Degrees Off Center" will be calculated by finding the differences between both center points. If this value is greater than 9\%, then a correction will be made. The calculation for this value can be found in section \ref{sec:anglecalc}.

\newpage

\begin{figure}[h]
    \centering
    \begin{tikzpicture}[node distance=2cm, shift={(-5, -10)}, scale=0.25]
        % Define nodes
        \node at (-5cm,0) (Camera) [circle, draw, xshift=-3cm] {\begin{minipage}{2cm} \centering
            Logitech Camera \\
            Input
          \end{minipage}};
        \node (Check) [diamond, draw, below of=Camera, yshift=-2cm, scale=0.8] {\begin{minipage}{3cm} \centering
            Image Captured \\
            Successfully by \\ Raspberry Pi
          \end{minipage}};
        \node (Objectdet) [rectangle, draw, below of=Check, yshift=-1cm] {Preform Object Detection};
        \node (Percent) [rectangle, draw, below of=Objectdet] {\begin{minipage}{3cm} \centering Perecent of \\ Screen Algorithm\end{minipage}};
        \node (EndDet) [rectangle, draw, left of=Check, xshift=-4cm] {Image Detection Ended};
        \node (Correc) [rectangle, draw, below of=Percent] {Preform Correction};
        \node (Send) [rectangle, draw, left of=Correc, xshift=-2cm] {Send To STM};
    
        % Define edges
        \draw [->] (Camera) -- node[right]{USB} (Check);
        \draw [->] (Check) -- node[right]{Yes} (Objectdet);
        \draw [->] (Objectdet) -- node[above]{} (Percent);
        \draw [->] (Check) -- node[above]{No} (EndDet);
        \draw [->] (Percent) -- node[right]{if $\geq 9\%$} (Correc);
        \draw [draw = thick,
         arrows={
         - 
           Stealth[length=8pt,open,bend,sep]}] (Correc) edge [bend right=95] (Objectdet);
        \draw [->] (Correc) -- (Send);

    \end{tikzpicture}
    \caption{Angle Correction Feedback Loop Flowchart}
    \label{fig:flowchart}
\end{figure}

\newpage

\subsubsection{Requirements and Verification}
\begin{center}
\begin{tabular}{ | m{20em} || m{20em} | } 
  \hline
  Requirements & Verification  \\ 
  \hline
  \hline
  Utilize OpenCV or OpenPose to determine $\Delta \theta$ of the child respective to the center of the robot.
  & 
  Ensure the OWB is at an idle state such that the wheels are not spinning. Then, stand slightly off-center from the front of the robot. While having the Raspberry Pi plugged into the monitor, display the video feed with overlayed boxes for the tracked object. Using an additional overlay on the video, there should be an angle that defines the degrees from the center of our target. Compared with the measured value.
  \\ 
  \hline
\end{tabular}
\end{center}

\subsection{Close-Range Object Detection System}
This subsystem encapsulates everything required to detect objects directly within the robot's path of travel. Upon activation of bumper-style limit switches on all sides of the robot, a signal will be sent to the Control Subsystem which will deactivate the motors and trigger an alert system. For more information regarding our choices of the commercial components that make up the Close-Range Object Detection Subsystem, please refer to section \ref{sec:cost}.

\subsubsection{Requirements and Verification}
\begin{center}
\begin{tabular}{ | m{20em} || m{20em} | } 
  \hline
  Requirements & Verification  \\ 
  \hline
  \hline
  The bumper-style limit switch should trigger an alert system and stop all motors until the bumper is depressed.
  & 
  Ensure the OWB is at an idle state such that the wheels are not spinning. Then, move the UWB tag such that the Robot must move to compensate for the change in the Tag's location. During the robot's travel, trigger one of the limit switches. The robot should stop and the alert system should trigger.
  \\ 
  \hline
\end{tabular}
\end{center}

\subsection{Control and Power Subsystem}
This subsystem encapsulates our main microcontroller and all power step-down converters to supply power to the individual components at the required levels. 

The Control subsystem will take in direction and angle vectors from the UWB Subsystem, and angle from Computer Vision Subsystem. We will then perform a sensor fusion where we place greater weight on the data provided by the UWB Subsystem, and allow for minor corrections through the Computer Vision Subsystem. This system will then decompose the direction and angles to obtain a direction vector which will be decomposed into individual wheel speeds as detailed in section \ref{sec:OWBKinematics}.

The Power Subsystem is responsible for supplying power to all other components of the robot. It will include a 12V battery and power distribution system. This subsystem will supply 12V power to the drive system. It will supply 5V to our STM32-based microcontroller, computer vision subsystem, and motor encoders. Lastly, it will supply 3.3V to the close-range object detection system and the UWB anchors. Refer to figure \ref{fig:Buck_12_5} for a calculation on stepping down from 12V to 5V and figure \ref{fig:Buck_12_3} for a calculation on stepping down from 12V to 3.3V.

\begin{figure}[H]
\begin{center}
    \\
    \caption{ Buck Converter Sizing 12V to 5V  } 
    \label{fig:Buck_12_5}
\end{center}
\end{figure}

\begin{figure}[H]
\begin{center}
    \\
    \caption{ Buck Converter Sizing 12V to 3.3V  } 
    \label{fig:Buck_12_3}
\end{center}
\end{figure}
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

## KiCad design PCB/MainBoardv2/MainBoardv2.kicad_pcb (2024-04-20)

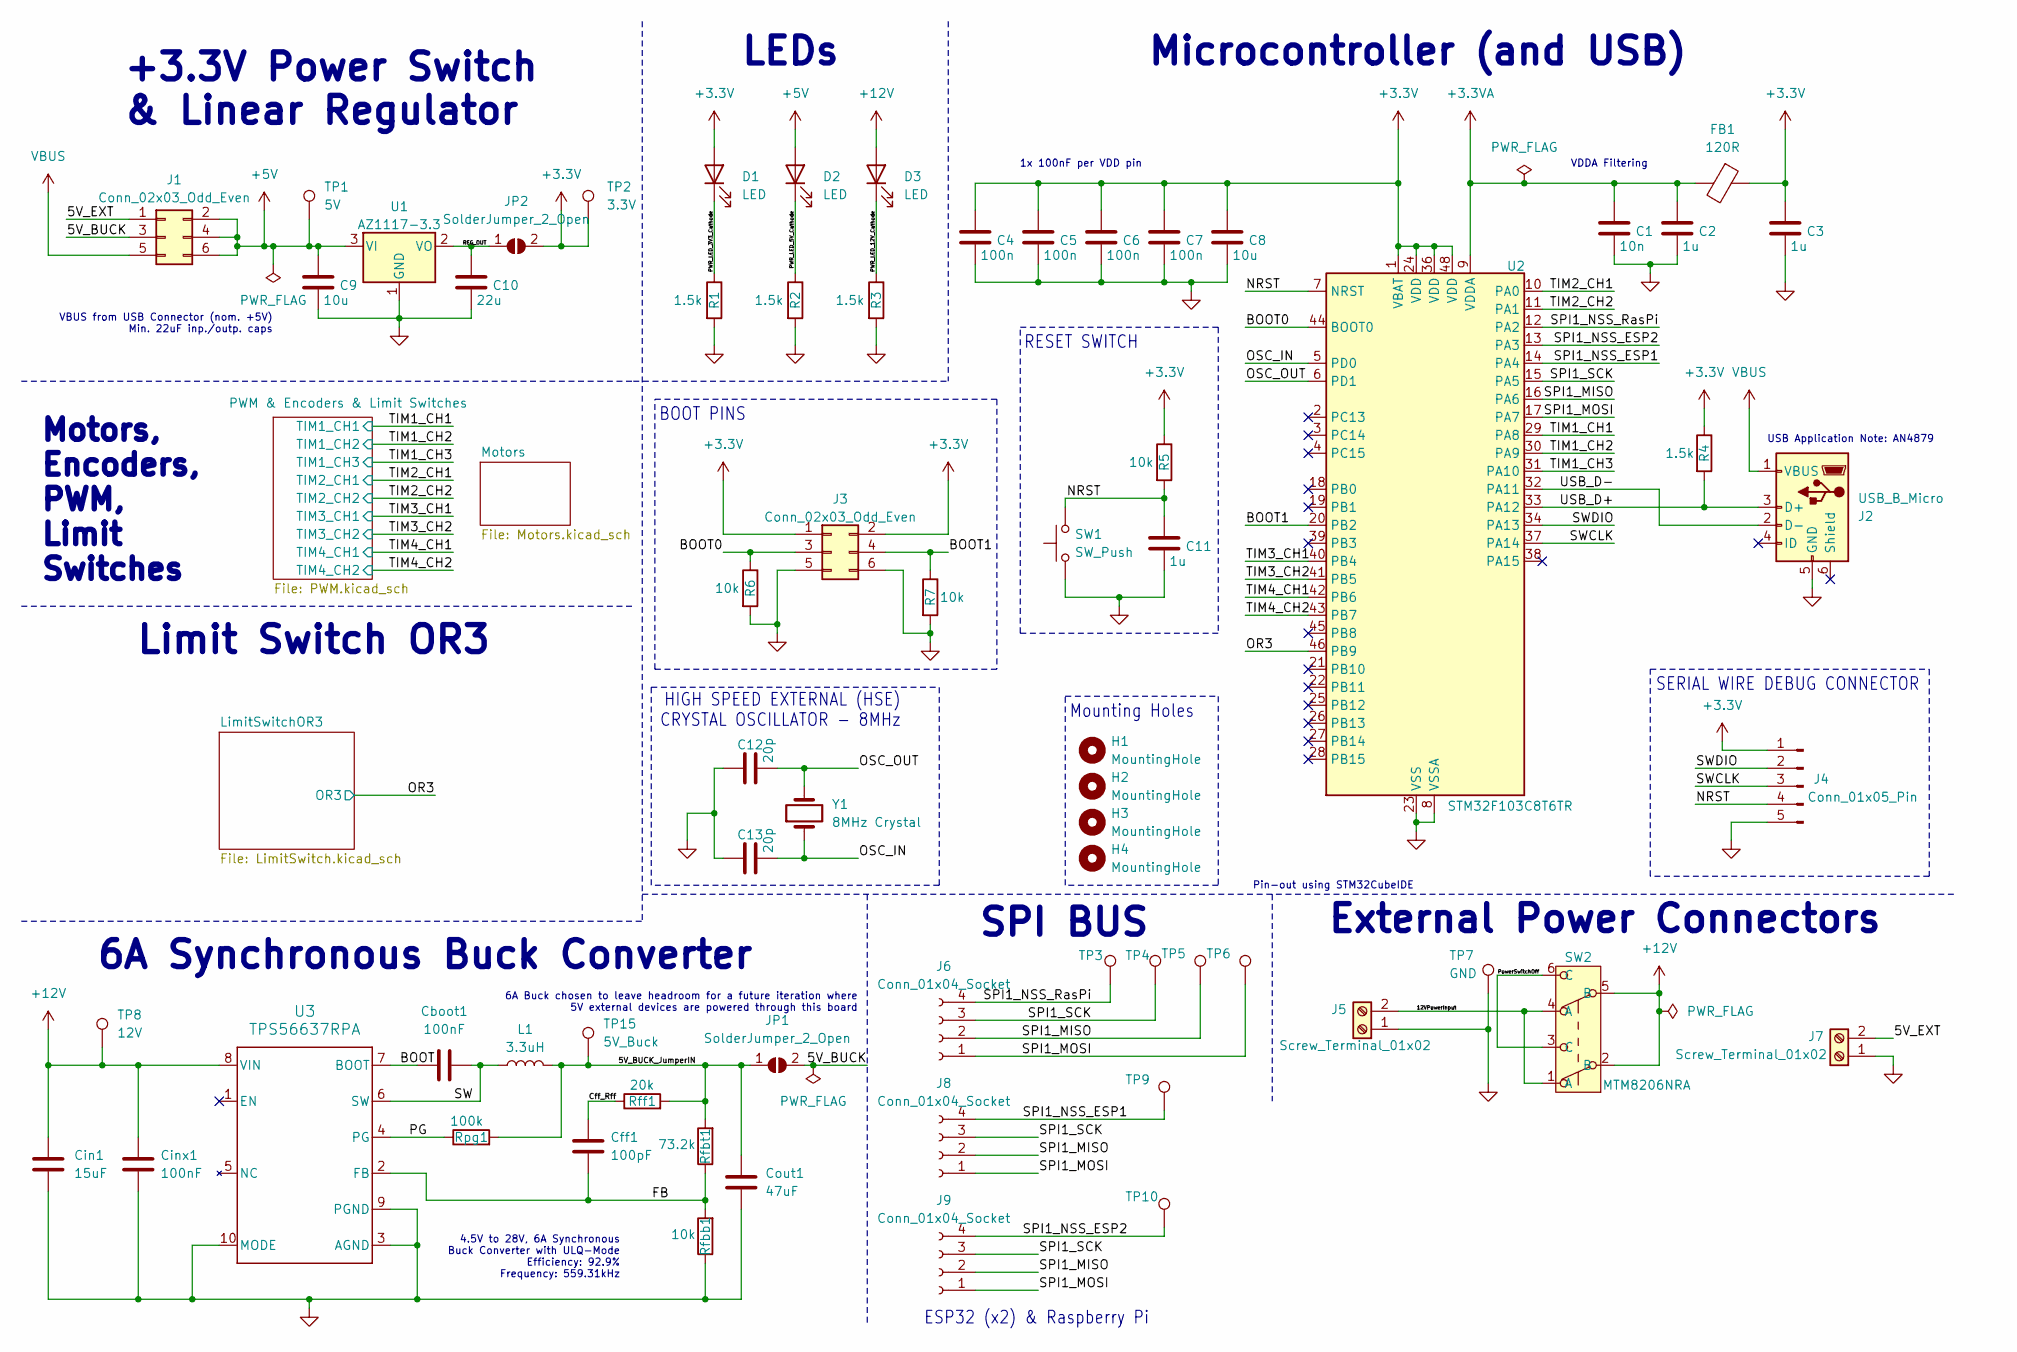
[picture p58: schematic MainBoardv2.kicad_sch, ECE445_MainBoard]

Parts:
C1: 10n; C_0603_1608Metric
C2, C3, C11: 1u; C_0603_1608Metric
C4, C5, C6, C7: 100n; C_0603_1608Metric
C8, C9: 10u; C_0603_1608Metric
C10: 22u; C_0805_2012Metric
C12, C13: 20p; C_0603_1608Metric
Cboot1: 100nF; C_0805_2012Metric
Cff1: 100pF; C_0805_2012Metric
Cin1: 15uF; C_0805_2012Metric
Cinx1: 100nF; C_0805_2012Metric
Cout1: 47uF; C_1210_3225Metric
D1, D2, D3: LED; LED_0603_1608Metric
FB1: 120R; L_0603_1608Metric
H1, H2, H3, H4: MountingHole; MountingHole_5mm
J1, J3: Conn_02x03_Odd_Even; PinHeader_2x03_P2.54mm_Vertical
J2: USB_B_Micro; AMPHENOL_10118192-0002LF
J4: Conn_01x05_Pin; PinSocket_1x05_P2.54mm_Vertical
J5, J7: Screw_Terminal_01x02; PHOENIX_1017521
J6, J8, J9: Conn_01x04_Socket; PinHeader_1x04_P2.54mm_Horizontal
JP1, JP2: SolderJumper_2_Open; SolderJumper-2_P1.3mm_Open_TrianglePad1.0x1.5mm
L1: 3.3uH; IHLP3232DZER3R3M01
R1, R2, R3, R4: 1.5k; R_0603_1608Metric
R5, R6, R7: 10k; R_0603_1608Metric
Rfbb1: 10k; R_0805_2012Metric
Rfbt1: 73.2k; R_0805_2012Metric
Rff1: 20k; R_0805_2012Metric
Rpg1: 100k; R_0805_2012Metric
SW1: SW_Push; SW_PUSH_6mm_H7.3mm
SW2: Toggle; MTM8206NRA
TP1: 5V; TestPoint_Keystone_5000-5004_Miniature
TP2: 3.3V; TestPoint_Keystone_5000-5004_Miniature
TP3, TP4, TP5, TP6, TP9, TP10: Orange; TestPoint_Keystone_5000-5004_Miniature
TP7: GND; TestPoint_Keystone_5000-5004_Miniature
TP8: 12V; TestPoint_Keystone_5000-5004_Miniature
TP15: 5V_Buck; TestPoint_Keystone_5000-5004_Miniature
U1: AZ1117-3.3; TO-252-2
U2: STM32F103C8T6TR; LQFP-48_7x7mm_P0.5mm
U3: TPS56637RPA; RPA0010A
Y1: 8MHz Crystal; Crystal_HC49-U_Vertical

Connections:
+3.3V: C3.1, C4.1, C5.1, C6.1, C7.1, C8.1, D1.2 (A), FB1.1, J3.1, J3.2, J4.1, JP2.2 (B), R4.1, R5.1, TP2.1, U2.1 (VBAT), U2.24 (VDD), U2.36 (VDD), U2.48 (VDD); also elsewhere on the board
+3.3VA: C1.1, C2.1, FB1.2, U2.9 (VDDA)
+5V: C9.1, D2.2 (A), J1.2, J1.4, J1.6, TP1.1, U1.3 (VI); also elsewhere on the board
+12V: Cin1.1, Cinx1.1, D3.2 (A), SW2.2 (B), SW2.5 (B), TP8.1, U3.8 (VIN); also elsewhere on the board
/5V_BUCK: J1.3, JP1.2 (B)
/5V_BUCK_JumperIN: Cout1.1, JP1.1 (A), L1.2, Rfbt1.2, Rff1.2, Rpg1.2, TP15.1
/5V_EXT: J1.1, J7.2
/12VPowerInput: J5.2, SW2.1 (A), SW2.4 (A)
/BOOT: Cboot1.1, U3.7 (BOOT)
/BOOT0: J3.3, R6.1, U2.44 (BOOT0)
/BOOT1: J3.4, R7.1, U2.20 (PB2)
/Cff_Rff: Cff1.1, Rff1.1
/FB: Cff1.2, Rfbb1.2, Rfbt1.1, U3.2 (FB)
/NRST: C11.1, J4.4, R5.2, SW1.2, U2.7 (NRST)
/OR3: U2.46 (PB9); also elsewhere on the board
/OSC_IN: C13.2, U2.5 (PD0), Y1.1
/OSC_OUT: C12.2, U2.6 (PD1), Y1.2
/PG: Rpg1.1, U3.4 (PG)
/PWR_LED_3V3_Cathode: D1.1 (K), R1.1
/PWR_LED_5V_Cathode: D2.1 (K), R2.1
/PWR_LED_12V_Cathode: D3.1 (K), R3.1
/PowerSwitchOff: SW2.3 (C), SW2.6 (C)
/REG_OUT: C10.1, JP2.1 (A), U1.2 (VO)
/SPI1_MISO: J6.2, J8.2, J9.2, TP5.1, U2.16 (PA6)
/SPI1_MOSI: J6.1, J8.1, J9.1, TP6.1, U2.17 (PA7)
/SPI1_NSS_ESP1: J8.4, TP9.1, U2.14 (PA4)
/SPI1_NSS_ESP2: J9.4, TP10.1, U2.13 (PA3)
/SPI1_NSS_RasPi: J6.4, TP3.1, U2.12 (PA2)
/SPI1_SCK: J6.3, J8.3, J9.3, TP4.1, U2.15 (PA5)
/SW: Cboot1.2, L1.1, U3.6 (SW)
/SWCLK: J4.3, U2.37 (PA14)
/SWDIO: J4.2, U2.34 (PA13)
/TIM1_CH1: U2.29 (PA8); also elsewhere on the board
/TIM1_CH2: U2.30 (PA9); also elsewhere on the board
/TIM1_CH3: U2.31 (PA10); also elsewhere on the board
/TIM2_CH1: U2.10 (PA0); also elsewhere on the board
/TIM2_CH2: U2.11 (PA1); also elsewhere on the board
/TIM3_CH1: U2.40 (PB4); also elsewhere on the board
/TIM3_CH2: U2.41 (PB5); also elsewhere on the board
/TIM4_CH1: U2.42 (PB6); also elsewhere on the board
/TIM4_CH2: U2.43 (PB7); also elsewhere on the board
/USB_D+: J2.3 (D+), R4.2, U2.33 (PA12)
/USB_D-: J2.2 (D-), U2.32 (PA11)
GND: C1.2, C2.2, C3.2, C4.2, C5.2, C6.2, C7.2, C8.2, C9.2, C10.2, C11.2, C12.1, C13.1, Cin1.2, Cinx1.2, Cout1.2, J2.5 (GND), J3.5, J3.6, J4.5, J5.1, J7.1, R1.2, R2.2, R3.2, R6.2, R7.2, Rfbb1.1, SW1.1, TP7.1, U1.1 (GND), U2.8 (VSSA), U2.23 (VSS), U2.35 (VSS), U2.47 (VSS), U3.3 (AGND), U3.9 (PGND), U3.10 (MODE); also elsewhere on the board
VBUS: J1.5, J2.1 (VBUS)

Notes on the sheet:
RESET SWITCH
Limit Switch OR3
SERIAL WIRE DEBUG CONNECTOR
BOOT PINS
VDDA Filtering
Microcontroller (and USB)
1x 100nF per VDD pin
External Power Connectors
LEDs
6A Buck chosen to leave headroom for a future iteration where 5V external devices are powered through this board
Pin-out using STM32CubeIDE
VBUS from USB Connector (nom. +5V) Min. 22uF inp./outp. caps
6A Synchronous Buck Converter
Motors, Encoders, PWM, Limit Switches
Mounting Holes
ESP32 (x2) & Raspberry Pi
USB Application Note: AN4879
4.5V to 28V, 6A Synchronous Buck Converter with ULQ-Mode Efficiency: 92.9% Frequency: 559.31kHz
SPI BUS
HIGH SPEED EXTERNAL (HSE) CRYSTAL OSCILLATOR - 8MHz
+3.3V Power Switch & Linear Regulator

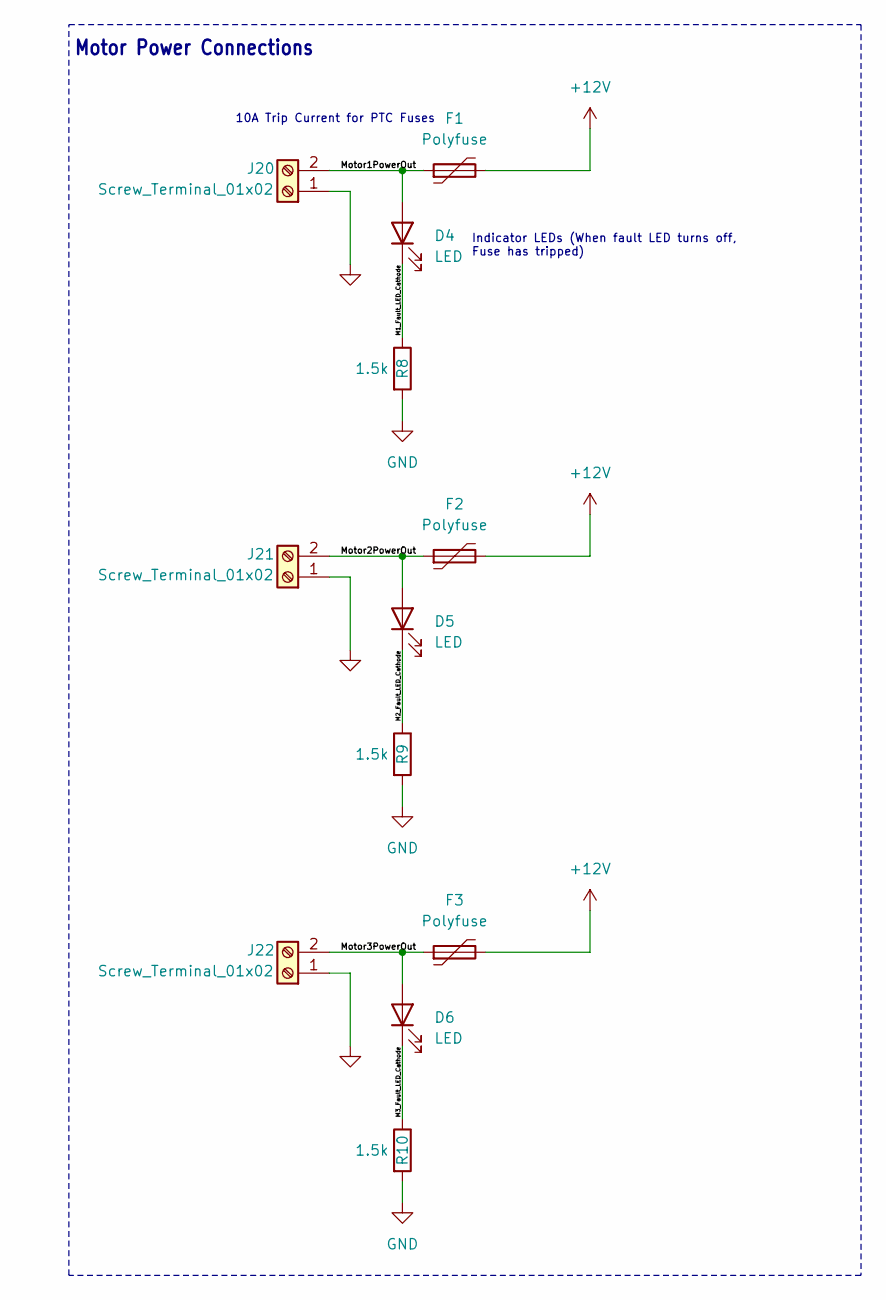
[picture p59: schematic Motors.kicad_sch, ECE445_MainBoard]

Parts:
D4, D5, D6: LED; LED_0603_1608Metric
F1, F2, F3: Polyfuse; Fuse_2920_7451Metric
J20, J21, J22: Screw_Terminal_01x02; PHOENIX_1017521
R8, R9, R10: 1.5k; R_0603_1608Metric

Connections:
+12V: F1.2, F2.2, F3.2; also elsewhere on the board
/Motors/M1_Fault_LED_Cathode: D4.1 (K), R8.1
/Motors/M2_Fault_LED_Cathode: D5.1 (K), R9.1
/Motors/M3_Fault_LED_Cathode: D6.1 (K), R10.1
/Motors/Motor1PowerOut: D4.2 (A), F1.1, J20.2
/Motors/Motor2PowerOut: D5.2 (A), F2.1, J21.2
/Motors/Motor3PowerOut: D6.2 (A), F3.1, J22.2
GND: J20.1, J21.1, J22.1, R8.2, R9.2, R10.2; also elsewhere on the board

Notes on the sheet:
Indicator LEDs (When fault LED turns off, Fuse has tripped)
Motor Power Connections
10A Trip Current for PTC Fuses

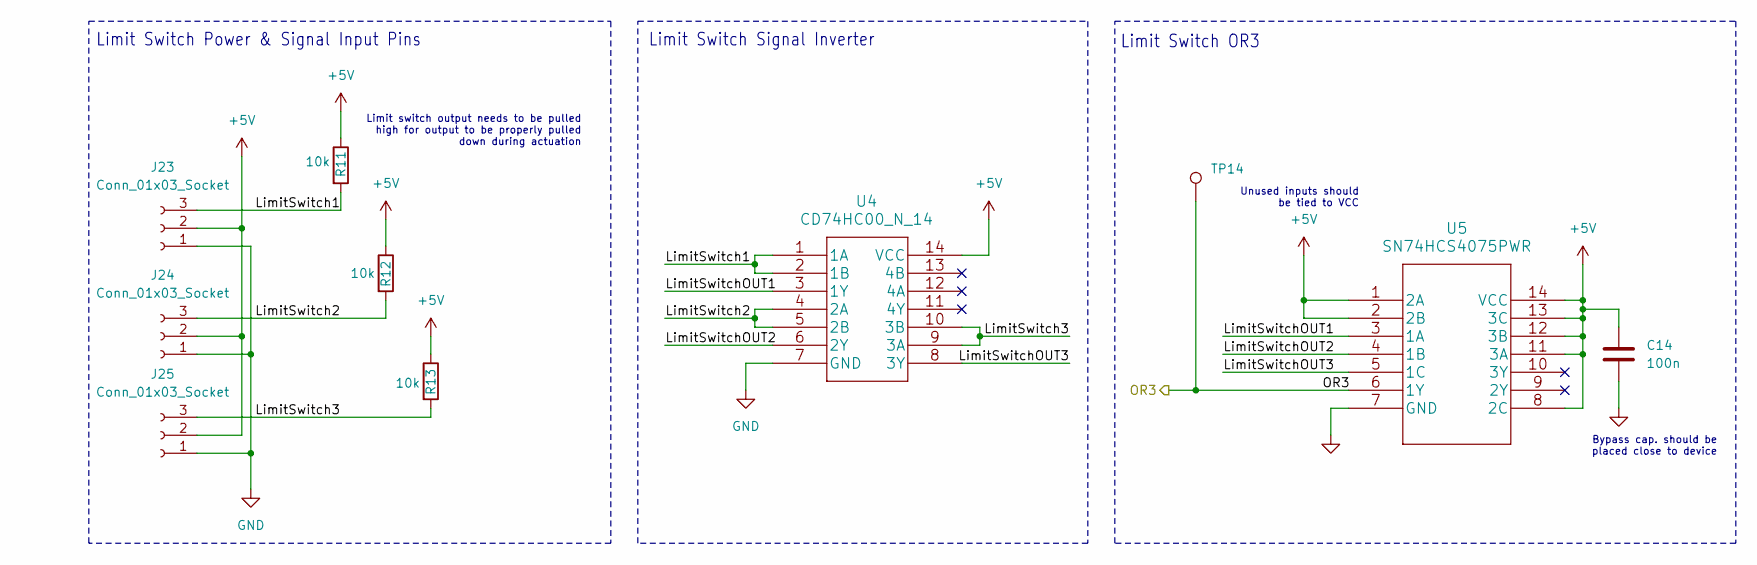
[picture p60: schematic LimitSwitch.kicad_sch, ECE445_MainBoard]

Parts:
C14: 100n; C_0603_1608Metric
J23, J24, J25: Conn_01x03_Socket; PinHeader_1x03_P2.54mm_Horizontal
R11, R12, R13: 10k; R_Axial_DIN0207_L6.3mm_D2.5mm_P7.62mm_Horizontal
TP14: White; TestPoint_Keystone_5000-5004_Miniature
U4: CD74HC00_N_14; DIP-14_W7.62mm_LongPads
U5: SN74HCS4075PWR

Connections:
+5V: C14.1, J23.2, J24.2, J25.2, R11.1, R12.1, R13.1, U4.14 (VCC), U5.1 (2A), U5.2 (2B), U5.8 (2C), U5.11 (3A), U5.12 (3B), U5.13 (3C), U5.14 (VCC); also elsewhere on the board
/LimitSwitchOR3/LimitSwitch1: J23.3, R11.2, U4.1 (1A), U4.2 (1B)
/LimitSwitchOR3/LimitSwitch2: J24.3, R12.2, U4.4 (2A), U4.5 (2B)
/LimitSwitchOR3/LimitSwitch3: J25.3, R13.2, U4.9 (3A), U4.10 (3B)
/LimitSwitchOR3/LimitSwitchOUT1: U4.3 (1Y), U5.3 (1A)
/LimitSwitchOR3/LimitSwitchOUT2: U4.6 (2Y), U5.4 (1B)
/LimitSwitchOR3/LimitSwitchOUT3: U4.8 (3Y), U5.5 (1C)
/OR3: TP14.1, U5.6 (1Y); also elsewhere on the board
GND: C14.2, J23.1, J24.1, J25.1, U4.7 (GND), U5.7 (GND); also elsewhere on the board

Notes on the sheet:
Bypass cap. should be placed close to device
Limit Switch OR3
Limit Switch Signal Inverter
Unused inputs should be tied to VCC
Limit switch output needs to be pulled high for output to be properly pulled down during actuation
Limit Switch Power & Signal Input Pins

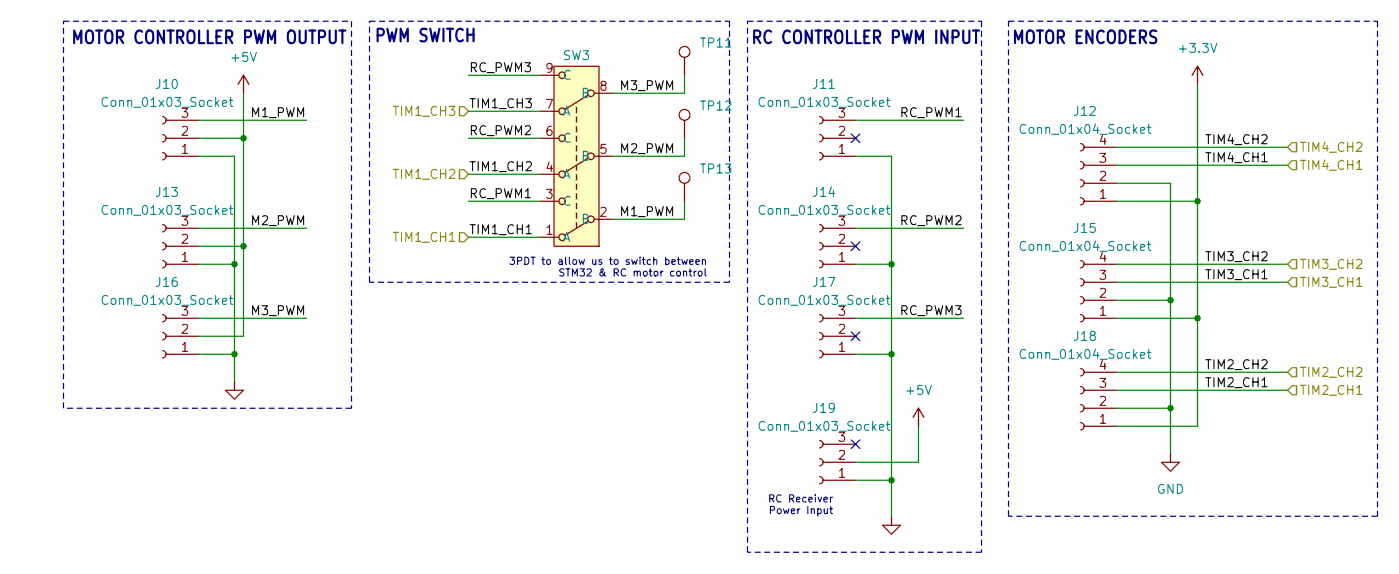
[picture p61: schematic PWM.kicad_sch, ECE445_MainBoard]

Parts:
J10, J13, J16: Conn_01x03_Socket; PinHeader_1x03_P2.54mm_Horizontal
J11, J14, J17, J19: Conn_01x03_Socket; PinHeader_1x03_P2.54mm_Vertical
J12, J15, J18: Conn_01x04_Socket; JST_PH_B4B-PH-K_1x04_P2.00mm_Vertical
SW3: Slide; SW_GF-161-0005
TP11, TP12, TP13: White; TestPoint_Keystone_5000-5004_Miniature

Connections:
+3.3V: J12.1, J15.1, J18.1; also elsewhere on the board
+5V: J10.2, J13.2, J16.2, J19.2; also elsewhere on the board
/PWM & Encoders & Limit Switches/M1_PWM: J10.3, SW3.2 (B), TP13.1
/PWM & Encoders & Limit Switches/M2_PWM: J13.3, SW3.5 (B), TP12.1
/PWM & Encoders & Limit Switches/M3_PWM: J16.3, SW3.8 (B), TP11.1
/PWM & Encoders & Limit Switches/RC_PWM1: J11.3, SW3.3 (C)
/PWM & Encoders & Limit Switches/RC_PWM2: J14.3, SW3.6 (C)
/PWM & Encoders & Limit Switches/RC_PWM3: J17.3, SW3.9 (C)
/TIM1_CH1: SW3.1 (A); also elsewhere on the board
/TIM1_CH2: SW3.4 (A); also elsewhere on the board
/TIM1_CH3: SW3.7 (A); also elsewhere on the board
/TIM2_CH1: J18.3; also elsewhere on the board
/TIM2_CH2: J18.4; also elsewhere on the board
/TIM3_CH1: J15.3; also elsewhere on the board
/TIM3_CH2: J15.4; also elsewhere on the board
/TIM4_CH1: J12.3; also elsewhere on the board
/TIM4_CH2: J12.4; also elsewhere on the board
GND: J10.1, J11.1, J12.2, J13.1, J14.1, J15.2, J16.1, J17.1, J18.2, J19.1; also elsewhere on the board

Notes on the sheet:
MOTOR ENCODERS
MOTOR CONTROLLER PWM OUTPUT
PWM SWITCH
RC Receiver Power Input
3PDT to allow us to switch between STM32 & RC motor control
RC CONTROLLER PWM INPUT

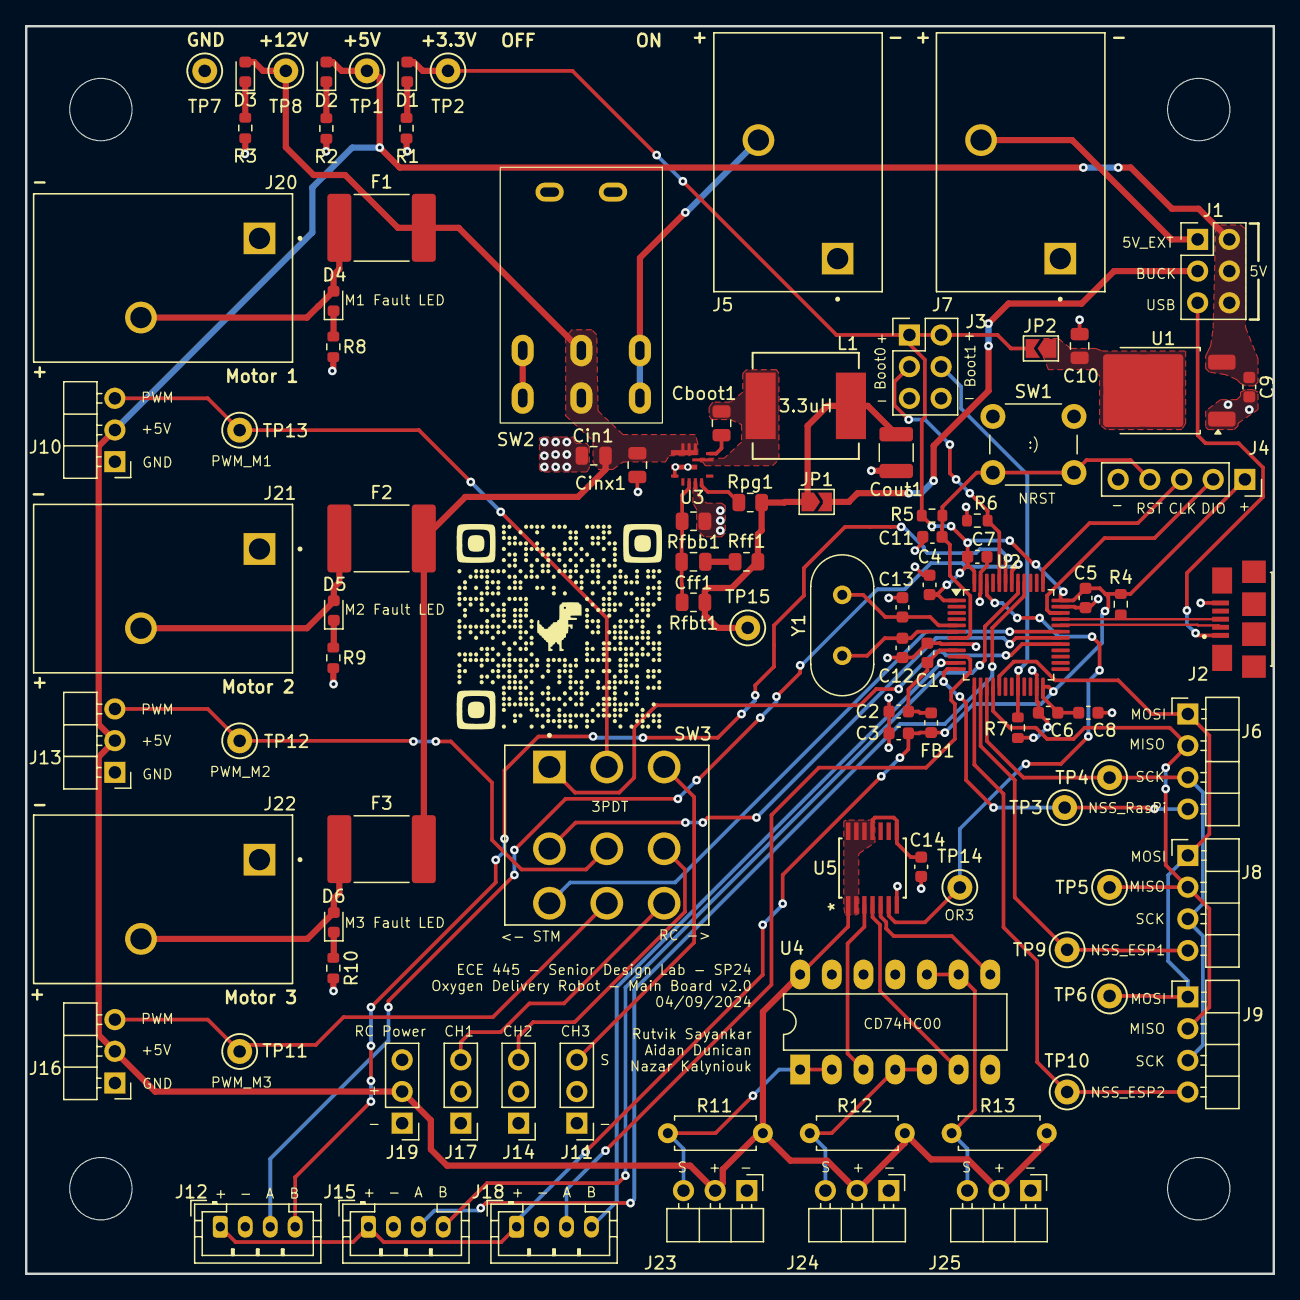
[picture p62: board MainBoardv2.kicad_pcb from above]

Board: 2 copper layers, 100.0 x 100.0 mm, 102 parts (0 on the bottom side), 63 nets.

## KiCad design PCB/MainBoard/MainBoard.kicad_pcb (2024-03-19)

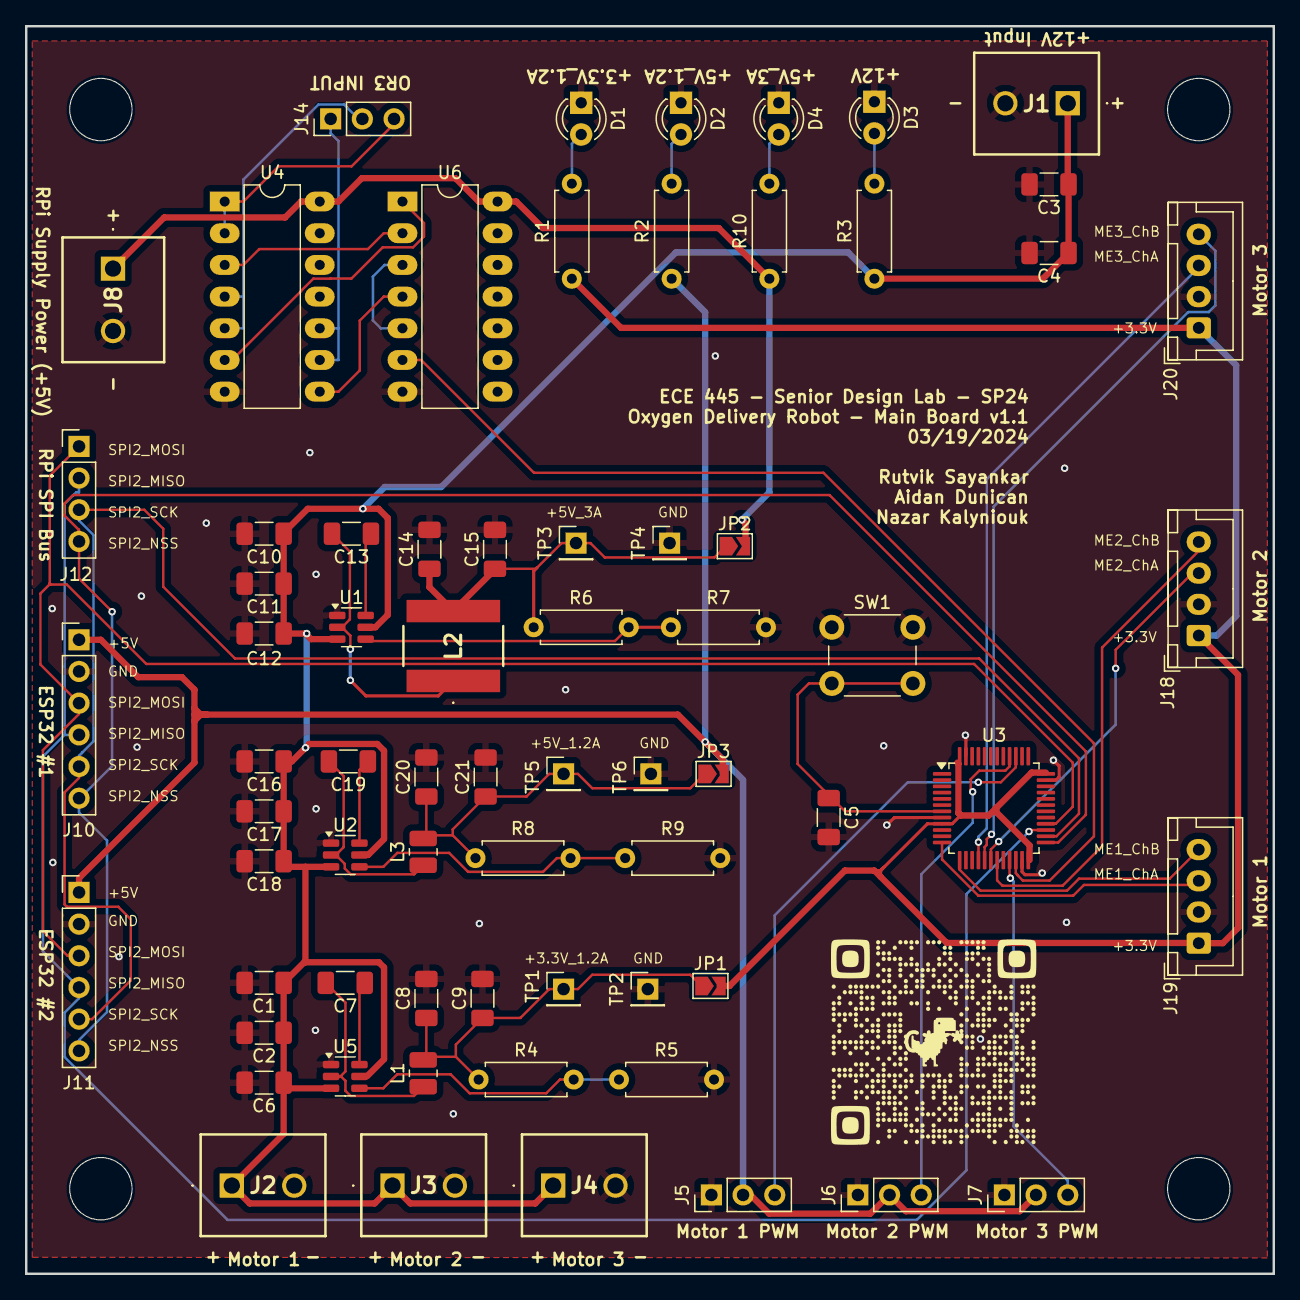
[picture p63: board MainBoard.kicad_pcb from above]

Board: 2 copper layers, 100.0 x 100.0 mm, 73 parts (0 on the bottom side), 43 nets.

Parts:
C1, C2, C10, C11, C16, C17: 10u; C_1206_3216Metric_Pad1.33x1.80mm_HandSolder
C3, C4, C5: 0.1uF; C_1206_3216Metric_Pad1.33x1.80mm_HandSolder
C6, C7, C12, C13, C18, C19: 100n; C_1206_3216Metric_Pad1.33x1.80mm_HandSolder
C8, C9, C14, C15, C20, C21: 33u; C_1206_3216Metric_Pad1.33x1.80mm_HandSolder
D1, D2, D3, D4: LED; LED_D3.0mm_Clear
H1, H2, H3, H4: MountingHole; MountingHole_5mm
J1, J2, J3, J4, J8: 5442170
J5, J6, J7, J14: Conn_01x03_Socket; PinHeader_1x03_P2.54mm_Vertical
J10, J11: Conn_01x06_Socket; PinHeader_1x06_P2.54mm_Vertical
J12: Conn_01x04_Socket; PinHeader_1x04_P2.54mm_Vertical
J18, J19, J20: Conn_01x04_Socket; JST_XH_B4B-XH-A_1x04_P2.50mm_Vertical
JP1, JP2, JP3: SolderJumper_2_Open; SolderJumper-2_P1.3mm_Open_TrianglePad1.0x1.5mm
L1: 4.7u; L_1008_2520Metric
L2: NRS8030T6R8MJGJ
L3: 5.6u; L_1008_2520Metric
R1, R2, R3, R10: 4.7k; R_Axial_DIN0207_L6.3mm_D2.5mm_P7.62mm_Horizontal
R4: 31.1k; R_Axial_DIN0207_L6.3mm_D2.5mm_P7.62mm_Horizontal
R5, R7, R9: 10k; R_Axial_DIN0207_L6.3mm_D2.5mm_P7.62mm_Horizontal
R6: 53.6k; R_Axial_DIN0207_L6.3mm_D2.5mm_P7.62mm_Horizontal
R8: 52.3k; R_Axial_DIN0207_L6.3mm_D2.5mm_P7.62mm_Horizontal
SW1: SW_Push; SW_PUSH_6mm_H7.3mm
TP1, TP2, TP3, TP4, TP5, TP6: TestPoint; PinHeader_1x01_P2.54mm_Vertical
U1, U2, U5: TPS56339DDC; SOT-23-6
U3: STM32F103C8Tx; LQFP-48_7x7mm_P0.5mm
U4, U6: CD74HC00_N_14; DIP-14_W7.62mm_LongPads

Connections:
+3.3V_1.2A: J18.1, J19.1, J20.1, JP1.2 (B), R1.1, U3.9 (VDDA), U3.24 (VDD), U3.36 (VDD), U3.48 (VDD)
+5V_1.2A: J5.2, J6.2, J7.2, J10.1, J11.1, JP3.2 (B), R2.1
+5V_3A: J8.1, JP2.2 (B), R10.1, U4.14 (VCC), U6.14 (VCC)
+12V: C1.1, C2.1, C3.1, C4.1, C6.1, C10.1, C11.1, C12.1, C16.1, C17.1, C18.1, J1.1, J2.1, J3.1, J4.1, R3.1, U1.3 (VIN), U1.5 (EN), U2.3 (VIN), U2.5 (EN), U5.3 (VIN), U5.5 (EN)
/LimitSwitchORGates/OR3 Output: U3.22 (PB11), U6.6 (2Y)
/ME1_ChA: J19.3, U3.12 (PA2)
/ME1_ChB: J19.4, U3.13 (PA3)
/ME2_ChA: J18.3, U3.18 (PB0)
/ME2_ChB: J18.4, U3.19 (PB1)
/ME3_ChA: J20.3, U3.16 (PA6)
/ME3_ChB: J20.4, U3.17 (PA7)
/SPI2_MISO: J10.4, J11.4, J12.2, U3.27 (PB14)
/SPI2_MOSI: J10.3, J11.3, J12.1, U3.28 (PB15)
/SPI2_NSS: J10.6, J11.6, J12.4, U3.25 (PB12)
/SPI2_SCK: J10.5, J11.5, J12.3, U3.26 (PB13)
GND: C1.2, C2.2, C3.2, C4.2, C5.2, C6.2, C8.2, C9.2, C10.2, C11.2, C12.2, C14.2, C15.2, C16.2, C17.2, C18.2, C20.2, C21.2, D1.1 (K), D2.1 (K), D3.1 (K), D4.1 (K), J1.2, J2.2, J3.2, J4.2, J5.1, J6.1, J7.1, J8.2, J10.2, J11.2, J18.2, J19.2, J20.2, R5.2, R7.2, R9.2, SW1.1, TP2.1, TP4.1, TP6.1, U1.1 (GND), U2.1 (GND), U3.8 (VSSA), U3.23 (VSS), U3.35 (VSS), U3.47 (VSS), U4.7 (GND), U5.1 (GND), U6.7 (GND)
unnamed: D1.2 (A), R1.2
unnamed: D2.2 (A), R2.2
unnamed: D3.2 (A), R3.2
unnamed: D4.2 (A), R10.2
unnamed: J5.3, U3.39 (PB3)
unnamed: J6.3, U3.40 (PB4)
unnamed: J7.3, U3.21 (PB10)
unnamed: J14.1, U4.9 (3A), U4.10 (3B)
unnamed: J14.2, U4.4 (2A), U4.5 (2B)
unnamed: J14.3, U4.1 (1A), U4.2 (1B)
unnamed: C8.1, C9.1, JP1.1 (A), L1.2, R4.1, TP1.1
unnamed: C14.1, C15.1, JP2.1 (A), L2.2, R6.1, TP3.1
unnamed: C20.1, C21.1, JP3.1 (A), L3.2, R8.1, TP5.1
unnamed: C13.1, U1.6 (BOOT)
unnamed: R6.2, R7.1, U1.4 (FB)
unnamed: C13.2, L2.1, U1.2 (SW)
unnamed: C19.1, U2.6 (BOOT)
unnamed: R8.2, R9.1, U2.4 (FB)
unnamed: C19.2, L3.1, U2.2 (SW)
unnamed: C5.1, SW1.2, U3.7 (NRST)
unnamed: U4.3 (1Y), U6.2 (1B)
unnamed: U4.6 (2Y), U6.1 (1A)
unnamed: U4.8 (3Y), U6.4 (2A)
unnamed: C7.1, U5.6 (BOOT)
unnamed: R4.2, R5.1, U5.4 (FB)
unnamed: C7.2, L1.1, U5.2 (SW)
unnamed: U6.3 (1Y), U6.5 (2B)

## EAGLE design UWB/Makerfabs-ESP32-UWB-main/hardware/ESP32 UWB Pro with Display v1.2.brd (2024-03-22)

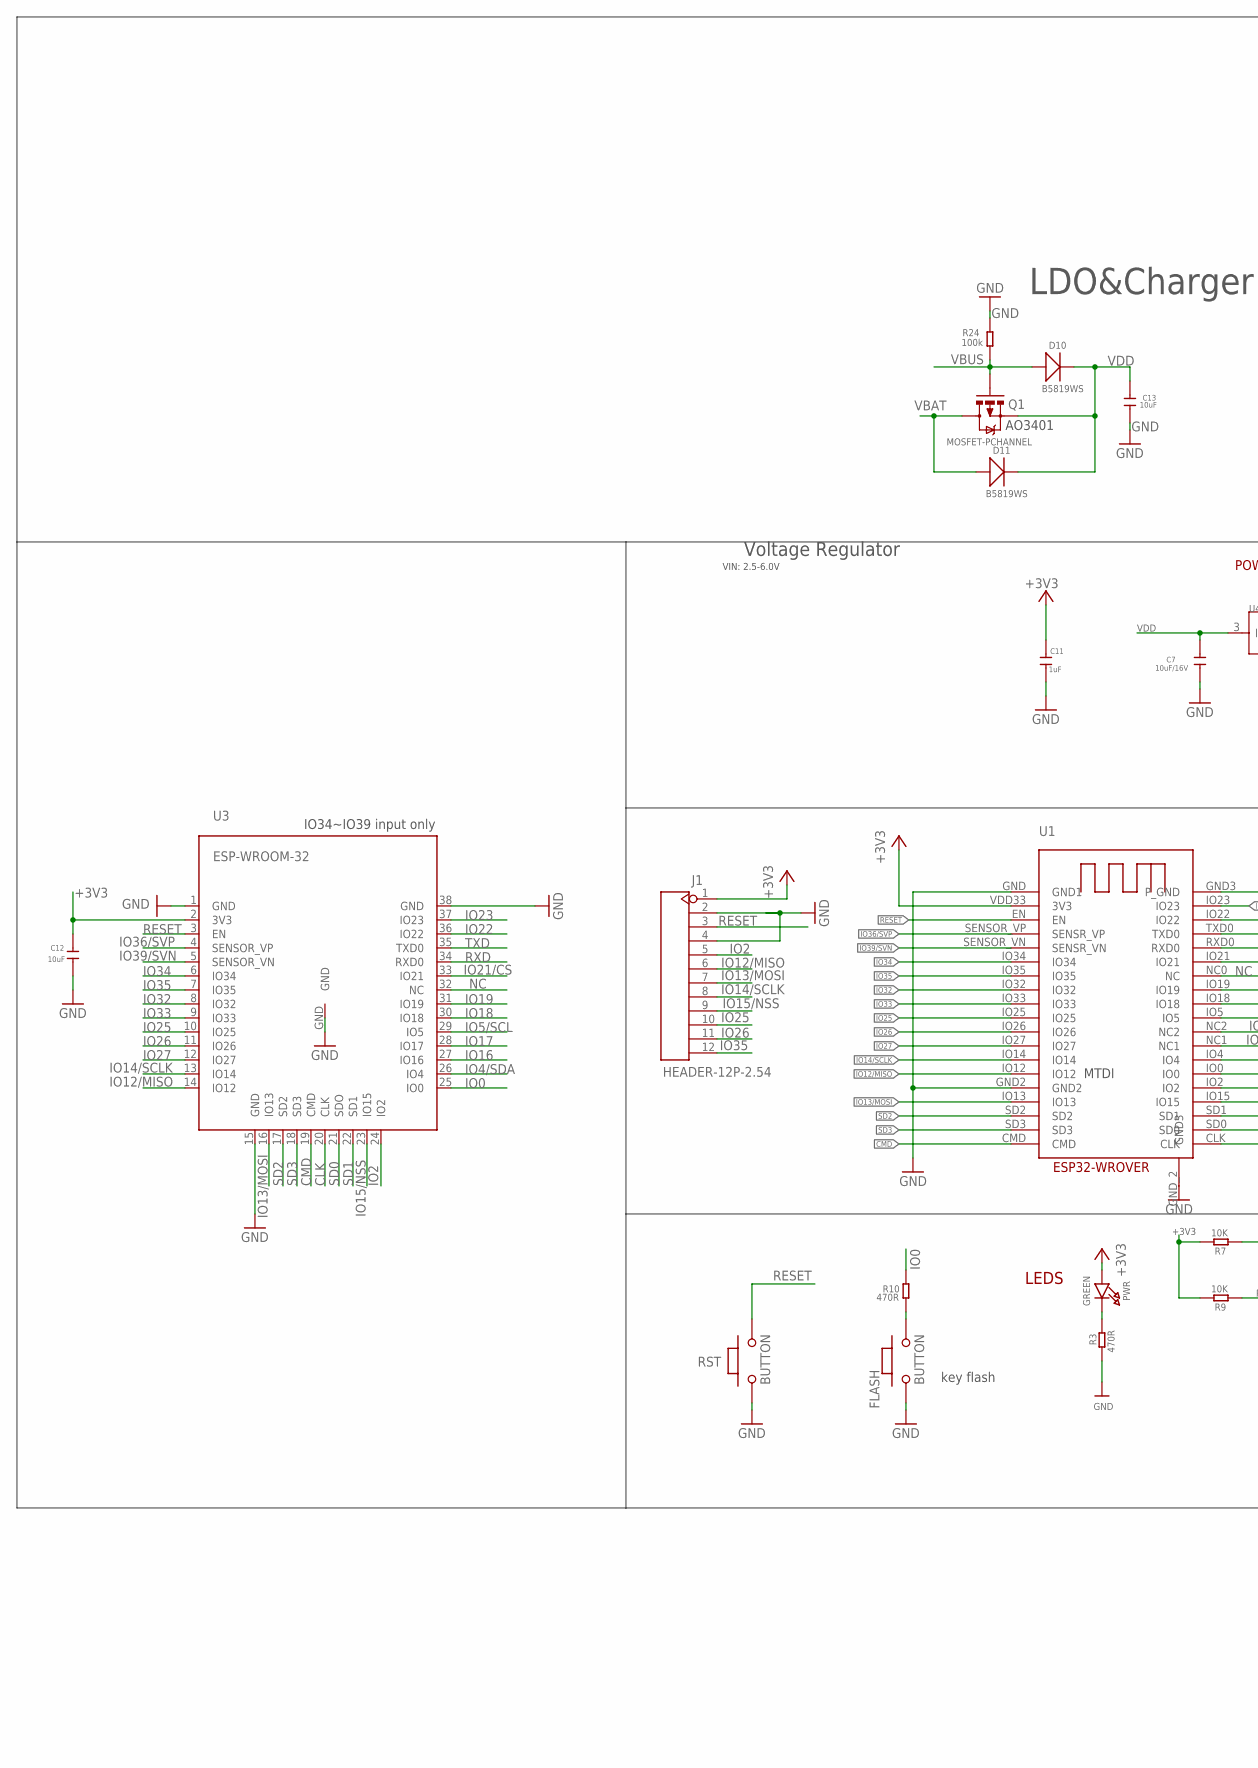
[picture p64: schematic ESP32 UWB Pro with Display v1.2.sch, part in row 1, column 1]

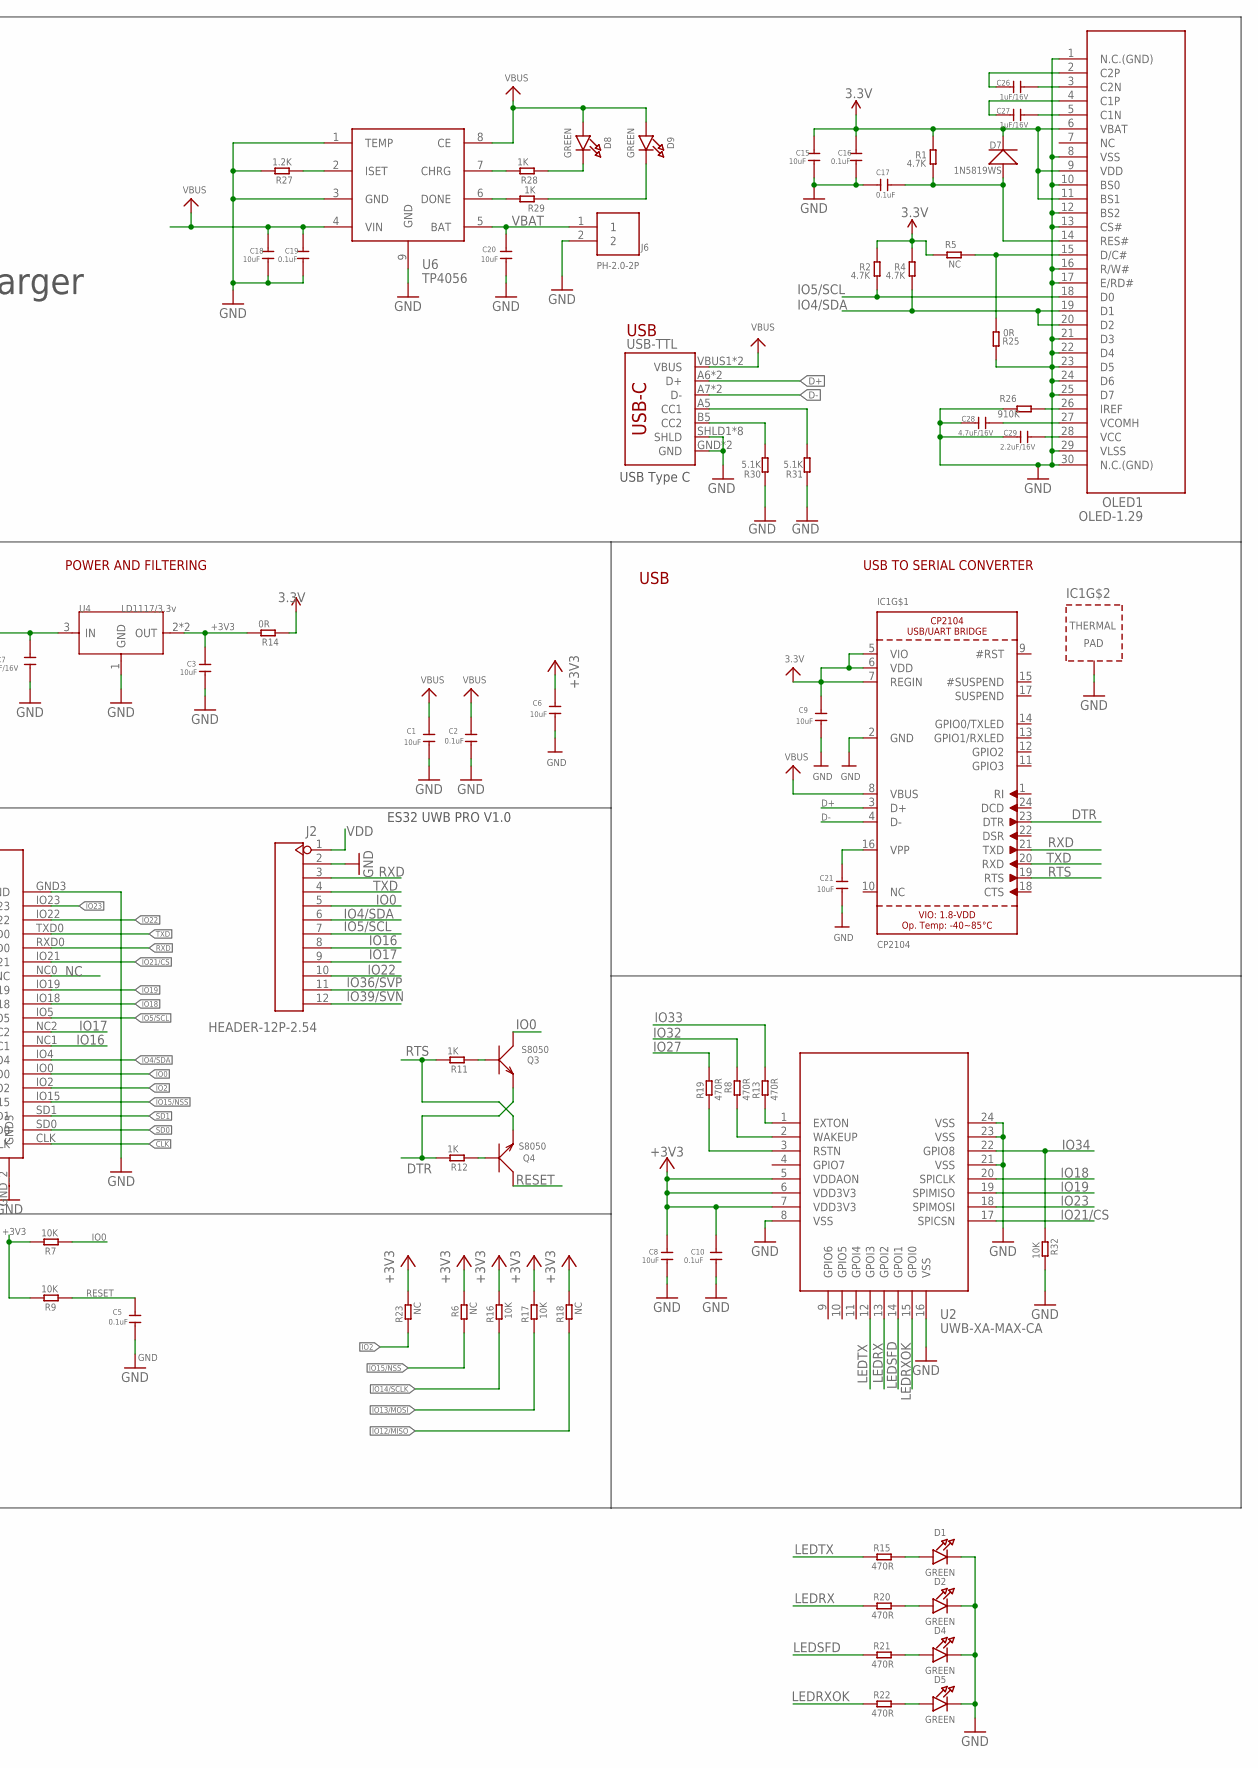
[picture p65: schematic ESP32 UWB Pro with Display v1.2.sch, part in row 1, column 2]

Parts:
C1, C3, C6, C8, C9, C12, C13, C15, C18, C20, C21: 10uF; 0603
C2, C5, C10, C16, C17, C19: 0.1uF; 0603
C7: 10uF/16V; 0603
C11: 1uF; 0603
C26, C27: 1uF/16V; 0603
C28: 4.7uF/16V; 0603
C29: 2.2uF/16V; 0603
D1, D2, D4, D5, D8, D9: GREEN; CHIPLED_0805_NOOUTLINE
D7: 1N5819WS; SOD323
D10, D11: B5819WS; SOD323
FLASH: BUTTON; 157SW
IC1: CP2104; QFN24_4MM_SMSC
J1, J2: HEADER-12P-2.54; 12P-2.54
J6: PH-2.0-2P
OLED1: OLED-1.29
PWR: GREEN; CHIPLED_0805_NOOUTLINE
Q1: MOSFET-PCHANNEL; SOT23-3
Q3, Q4: S8050; SOT23
R1, R2, R4: 4.7K; R0603
R3, R8, R10, R13, R15, R19, R20, R21, R22: 470R; R0603
R5, R6, R18, R23: NC; R0603
R7, R9, R16, R17, R32: 10K; R0603
R11, R12, R28, R29: 1K; R0603
R14, R25: 0R; R0603
R24: 100k; R0603
R26: 910K; R0603
R27: 1.2K; R0603
R30, R31: 5.1K; DISCRETE_R0603
RST: BUTTON; 157SW
U1: ESP32-WROVER
U2: UWB-XA-MAX-CA; UWB-X1-MAK-CA
U3: ESP-WROOM-32
U4: LD1117/3.3v; SOT89
U6: TP4056; SOP8-1.27P
USB-TTL: USB_C5; USB-C-16P-5

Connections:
3.3V: C15.1, C16.1, D7.-, OLED1.6 (VBAT), OLED1.9 (VDD), OLED1.11 (BS1), R1.2, R2.2, R4.2, R5.2, R14.1
+3V3: C3.1, C6.1, C8.1, C9.1, C10.1, C11.1, C12.1, IC1.5 (VIO), IC1.6 (VDD), IC1.7 (REGIN), J1.1, PWR.A, R6.2, R7.2, R9.2, R14.2, R16.2, R17.2, R18.2, R23.2, U1.VDD33 (3V3), U2.5 (VDDAON), U2.6 (VDD3V3), U2.7 (VDD3V3), U3.2 (3V3), U4.2 (OUT), U4.4 (OUT)
CLK: U1.CLK, U3.20 (CLK)
CMD: U1.CMD, U3.19 (CMD)
D+: IC1.3 (D+), USB-TTL.A6 (D+), USB-TTL.B6 (D+)
D-: IC1.4 (D-), USB-TTL.A7 (D-), USB-TTL.B7 (D-)
DTR: IC1.23 (DTR), Q3.2 (E), R12.2
GND: C1.2, C2.2, C3.2, C5.2, C6.2, C7.2, C8.2, C9.2, C10.2, C11.2, C12.2, C13.1, C15.2, C16.2, C17.1, C18.2, C19.2, C20.2, C21.2, C28.1, C29.1, D1.C, D2.C, D4.C, D5.C, FLASH.1, IC1.2 (GND), IC1.THERM (TP), J1.2, J1.4, J2.2, J6.2, OLED1.1 (N.C.(GND)), OLED1.8 (VSS), OLED1.10 (BS0), OLED1.12 (BS2), OLED1.13 (CS#), OLED1.16 (R/W#), OLED1.17 (E/RD#), OLED1.21 (D3), OLED1.22 (D4), OLED1.23 (D5), OLED1.24 (D6), OLED1.25 (D7), OLED1.29 (VLSS), OLED1.30 (N.C.(GND)), R3.1, R24.2, R25.2, R26.2, R27.2, R30.1, R31.1, R32.2, RST.1, U1.GND (GND1), U1.GND2, U1.GND3 (P_GND), U1.GND_2 (GND3), U2.8 (VSS), U2.16 (VSS), U2.21 (VSS), U2.23 (VSS), U2.24 (VSS), U3.1 (GND), U3.15 (GND), U3.38 (GND), U3.GND, U4.1 (GND), U6.1 (TEMP), U6.3 (GND), U6.9 (GND), USB-TTL.GND, USB-TTL.GND2 (GND), USB-TTL.SHLD1 (SHLD), USB-TTL.SHLD2 (SHLD), USB-TTL.SHLD3 (SHLD), USB-TTL.SHLD4 (SHLD), USB-TTL.SHLD5 (SHLD), USB-TTL.SHLD6 (SHLD), USB-TTL.SHLD7 (SHLD), USB-TTL.SHLD8 (SHLD)
IO0: J2.5, Q3.3 (C), R7.1, R10.2, U1.IO0, U3.25 (IO0)
IO2: J1.5, R23.1, U1.IO2, U3.24 (IO2)
IO4/SDA: J2.6, OLED1.19 (D1), OLED1.20 (D2), R4.1, U1.IO4, U3.26 (IO4)
IO5/SCL: J2.7, OLED1.18 (D0), R2.1, U1.IO5, U3.29 (IO5)
IO12/MISO: J1.6, R18.1, U1.IO12, U3.14 (IO12)
IO13/MOSI: J1.7, R17.1, U1.IO13, U3.16 (IO13)
IO14/SCLK: J1.8, R16.1, U1.IO14, U3.13 (IO14)
IO15/NSS: J1.9, R6.1, U1.IO15, U3.23 (IO15)
IO16: J2.8, U1.NC1, U3.27 (IO16)
IO17: J2.9, U1.NC2, U3.28 (IO17)
IO18: U1.IO18, U2.20 (SPICLK), U3.30 (IO18)
IO19: U1.IO19, U2.19 (SPIMISO), U3.31 (IO19)
IO21/CS: U1.IO21, U2.17 (SPICSN), U3.33 (IO21)
IO22: J2.10, U1.IO22, U3.36 (IO22)
IO23: U1.IO23, U2.18 (SPIMOSI), U3.37 (IO23)
IO25: J1.10, U1.IO25, U3.10 (IO25)
IO26: J1.11, U1.IO26, U3.11 (IO26)
IO27: R19.2, U1.IO27, U3.12 (IO27)
IO32: R8.2, U1.IO32, U3.8 (IO32)
IO33: R13.2, U1.IO33, U3.9 (IO33)
IO34: R32.1, U1.IO34, U2.22 (GPIO8), U3.6 (IO34)
IO35: J1.12, U1.IO35, U3.7 (IO35)
IO36/SVP: J2.11, U1.SENSOR_VP (SENSR_VP), U3.4 (SENSOR_VP)
IO39/SVN: J2.12, U1.SENSOR_VN (SENSR_VN), U3.5 (SENSOR_VN)
LEDRX: R20.1, U2.13 (GPOI2)
LEDRXOK: R22.1, U2.15 (GPOI0)
LEDSFD: R21.1, U2.14 (GPOI1)
LEDTX: R15.1, U2.12 (GPOI3)
unnamed: D1.A, R15.2
unnamed: C21.1, IC1.16 (VPP)
unnamed: C17.2, D7.+, OLED1.14 (RES#), R1.1
unnamed: OLED1.15 (D/C#), R5.1, R25.1
unnamed: PWR.C, R3.2
unnamed: C28.2, OLED1.27 (VCOMH)
unnamed: C26.2, OLED1.3 (C2N)
unnamed: C29.2, OLED1.28 (VCC)
unnamed: OLED1.26 (IREF), R26.1
unnamed: R13.1, U2.1 (EXTON)
unnamed: R8.1, U2.2 (WAKEUP)
unnamed: R19.1, U2.3 (RSTN)
unnamed: Q4.1 (B), R12.1
unnamed: Q3.1 (B), R11.1
unnamed: FLASH.2, R10.1
unnamed: D2.A, R20.2
unnamed: D4.A, R21.2
unnamed: D5.A, R22.2
unnamed: C26.1, OLED1.2 (C2P)
unnamed: C27.1, OLED1.4 (C1P)
unnamed: C27.2, OLED1.5 (C1N)
unnamed: R27.1, U6.2 (ISET)
unnamed: R31.2, USB-TTL.A5 (CC1)
unnamed: R30.2, USB-TTL.B5 (CC2)
unnamed: R28.2, U6.7 (CHRG)
unnamed: R29.2, U6.6 (DONE)
unnamed: D8.C, R28.1
unnamed: D9.C, R29.1
NC: U1.NC0 (NC), U3.32 (NC)
RESET: C5.1, J1.3, Q4.3 (C), R9.1, RST.2, U1.EN, U3.3 (EN)
RTS: IC1.19 (RTS), Q4.2 (E), R11.2
RXD: IC1.21 (TXD), J2.3, U1.RXD0, U3.34 (RXD0)
SD0: U1.SD0, U3.21 (SDO)
SD1: U1.SD1, U3.22 (SD1)
SD2: U1.SD2, U3.17 (SD2)
SD3: U1.SD3, U3.18 (SD3)
TXD: IC1.20 (RXD), J2.4, U1.TXD0, U3.35 (TXD0)
VBAT: C20.1, D11.+, J6.1, Q1.3 (D), U6.5 (BAT)
VBUS: C1.1, C2.1, C18.1, C19.1, D8.A, D9.A, D10.+, IC1.8 (VBUS), Q1.1 (G), R24.1, U6.4 (VIN), U6.8 (CE), USB-TTL.VBUS1 (VBUS), USB-TTL.VBUS2 (VBUS)
VDD: C7.1, C13.2, D10.-, D11.-, J2.1, Q1.2 (S), U4.3 (IN)

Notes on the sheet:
USB
LEDS
POWER AND FILTERING
USB TO SERIAL CONVERTER
key flash
ES32 UWB PRO V1.0
MTDI
IO34~IO39 input only
Voltage Regulator
VIN: 2.5-6.0V
USB Type C
LDO&Charger
AO3401

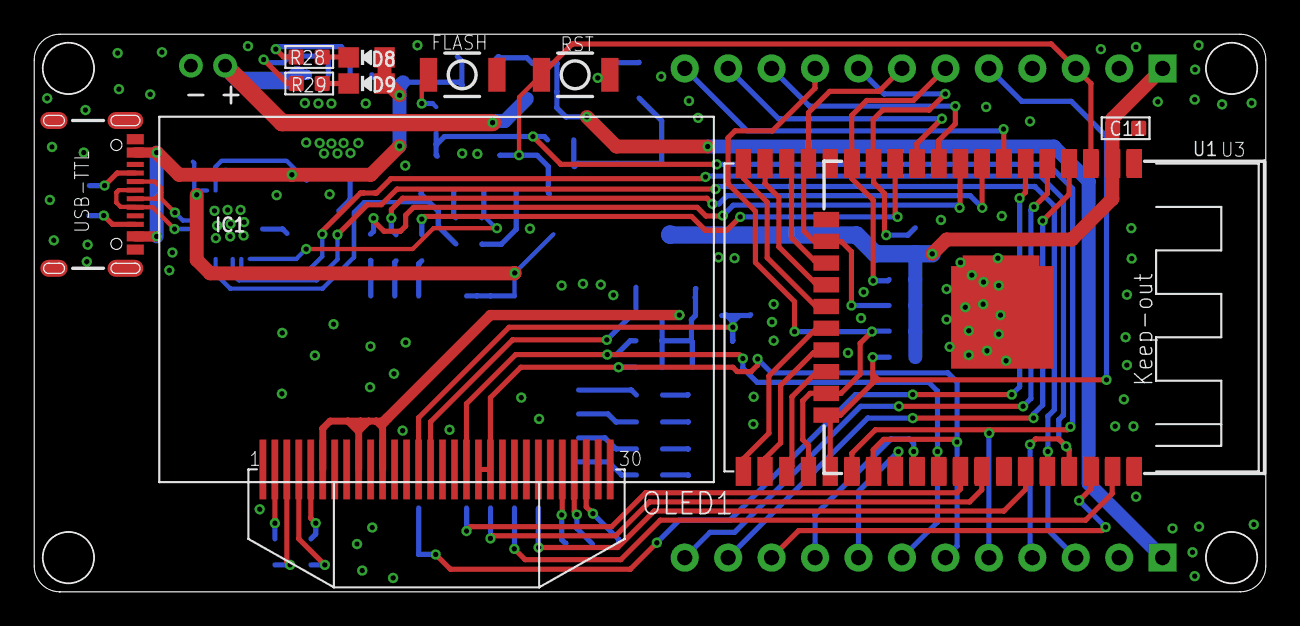
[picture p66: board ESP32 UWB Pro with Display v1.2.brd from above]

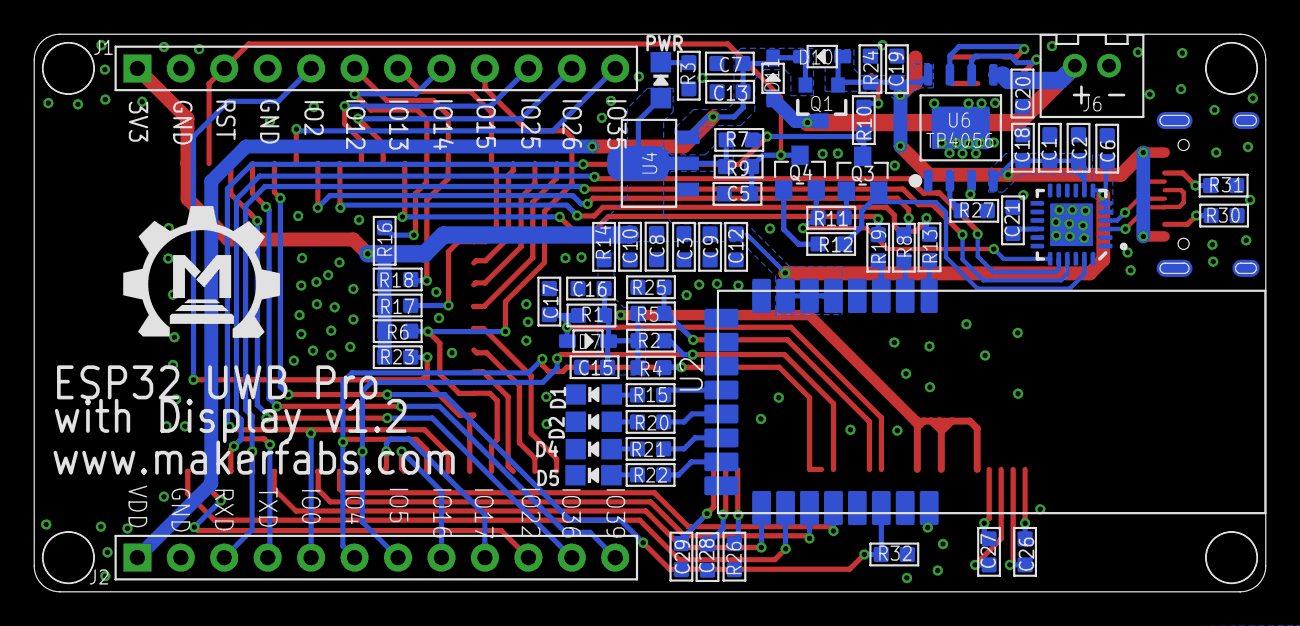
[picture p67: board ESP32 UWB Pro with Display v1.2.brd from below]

Board: 2 copper layers, 72.0 x 32.6 mm, 82 parts (71 on the bottom side), 76 nets.

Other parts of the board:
U$1: MAKERFABS_0.3

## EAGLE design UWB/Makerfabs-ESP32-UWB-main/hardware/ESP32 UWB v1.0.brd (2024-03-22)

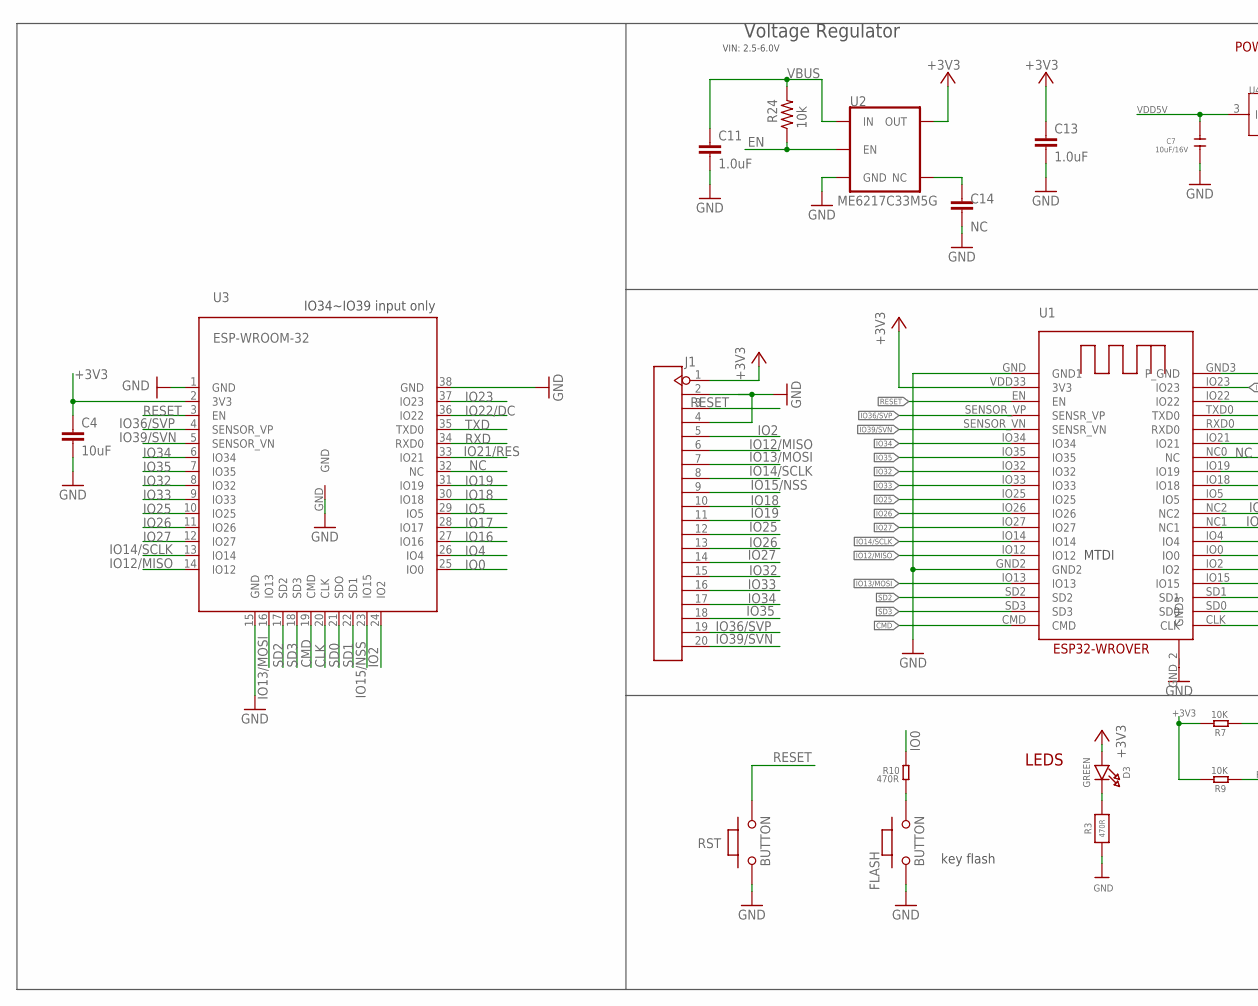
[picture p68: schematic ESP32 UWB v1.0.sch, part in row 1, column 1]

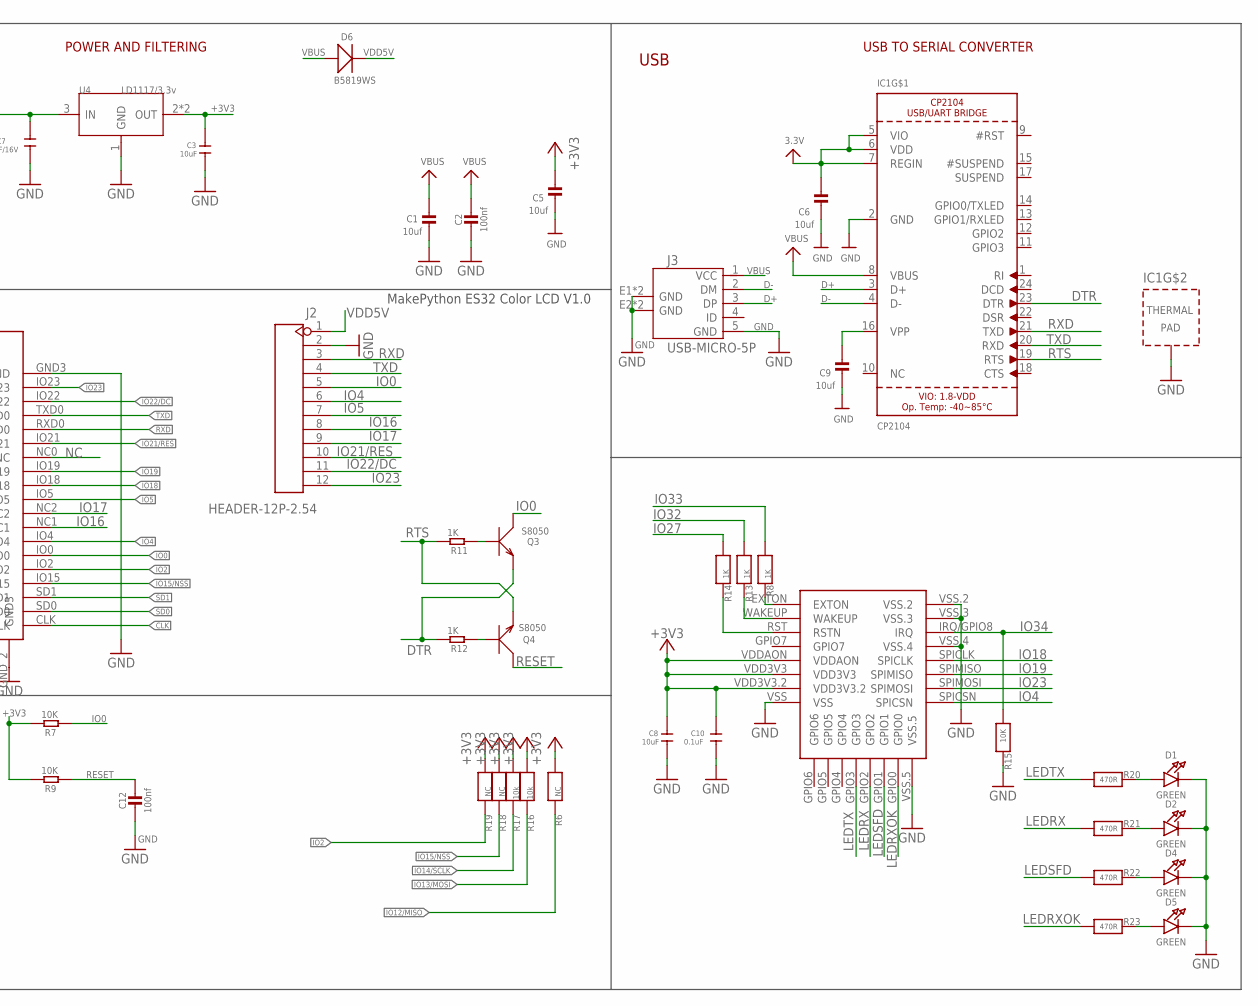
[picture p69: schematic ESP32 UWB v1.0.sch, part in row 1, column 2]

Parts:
C1, C5, C6, C9: 10uf; 0603-NO
C2, C12: 100nf; 0603-NO
C3, C4, C8: 10uF; C0603
C7: 10uF/16V; C0603
C10: 0.1uF; C0603
C11, C13: 1.0uF; 0603
C14: NC; 0603
D1, D2, D3, D4, D5: GREEN; CHIPLED_0805_NOOUTLINE
D6: B5819WS; SOD323
FLASH: BUTTON; 157SW
IC1: CP2104; QFN24_4MM_SMSC
J1: HEADER-20P-2.54; 20P-2.54
J2: HEADER-12P-2.54; 12P-2.54
J3: USB-MICRO-5P; MICRO-USB-5P
Q3, Q4: S8050; SOT23
R3, R20, R21, R22, R23: 470R; 0603-NO
R6, R18, R19: NC; 0603-NO
R7, R9: 10K; 0603
R8, R13, R14: 1K; 0603-NO
R10: 470R; 0603
R11, R12: 1K; 0603
R15: 10K; 0603-NO
R16, R17: 10k; 0603-NO
R24: 10k; 0603
RST: BUTTON; 157SW
U1: ESP32-WROVER
U2: ME6217C33M5G; SOT23-5
U3: ESP-WROOM-32
U4: LD1117/3.3v; SOT89
U5: DWM1000

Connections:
+3V3: C3.1, C4.1, C5.1, C6.1, C8.1, C10.1, C13.1, D3.A, IC1.5 (VIO), IC1.6 (VDD), IC1.7 (REGIN), J1.1, R6.1, R7.2, R9.2, R16.1, R17.1, R18.1, R19.1, U1.VDD33 (3V3), U2.5 (OUT), U3.2 (3V3), U4.2 (OUT), U4.4 (OUT), U5.VDD3V3, U5.VDD3V3.2, U5.VDDAON
CLK: U1.CLK, U3.20 (CLK)
CMD: U1.CMD, U3.19 (CMD)
D+: IC1.3 (D+), J3.3 (DP)
D-: IC1.4 (D-), J3.2 (DM)
DTR: IC1.23 (DTR), Q3.2 (E), R12.2
EN: R24.1, U2.3 (EN)
GND: C1.2, C2.2, C3.2, C4.2, C5.2, C6.2, C7.2, C8.2, C9.2, C10.2, C11.2, C12.2, C13.2, C14.2, D1.C, D2.C, D4.C, D5.C, FLASH.1, IC1.2 (GND), IC1.THERM (TP), J1.2, J1.4, J2.2, J3.5 (GND), J3.E1 (GND), J3.E2 (GND), J3.P1 (GND), J3.P2 (GND), R3.1, R15.2, RST.1, U1.GND (GND1), U1.GND2, U1.GND3 (P_GND), U1.GND_2 (GND3), U2.2 (GND), U3.1 (GND), U3.15 (GND), U3.38 (GND), U3.GND, U4.1 (GND), U5.VSS, U5.VSS.2, U5.VSS.3, U5.VSS.4, U5.VSS.5
IO0: J2.5, Q3.3 (C), R7.1, R10.2, U1.IO0, U3.25 (IO0)
IO2: J1.5, R19.2, U1.IO2, U3.24 (IO2)
IO4: J2.6, U1.IO4, U3.26 (IO4), U5.SPICSN
IO5: J2.7, U1.IO5, U3.29 (IO5)
IO12/MISO: J1.6, R6.2, U1.IO12, U3.14 (IO12)
IO13/MOSI: J1.7, R16.2, U1.IO13, U3.16 (IO13)
IO14/SCLK: J1.8, R17.2, U1.IO14, U3.13 (IO14)
IO15/NSS: J1.9, R18.2, U1.IO15, U3.23 (IO15)
IO16: J2.8, U1.NC1, U3.27 (IO16)
IO17: J2.9, U1.NC2, U3.28 (IO17)
IO18: J1.10, U1.IO18, U3.30 (IO18), U5.SPICLK
IO19: J1.11, U1.IO19, U3.31 (IO19), U5.SPIMISO
IO21/RES: J2.10, U1.IO21, U3.33 (IO21)
IO22/DC: J2.11, U1.IO22, U3.36 (IO22)
IO23: J2.12, U1.IO23, U3.37 (IO23), U5.SPIMOSI
IO25: J1.12, U1.IO25, U3.10 (IO25)
IO26: J1.13, U1.IO26, U3.11 (IO26)
IO27: J1.14, R14.1, U1.IO27, U3.12 (IO27)
IO32: J1.15, R13.1, U1.IO32, U3.8 (IO32)
IO33: J1.16, R8.1, U1.IO33, U3.9 (IO33)
IO34: J1.17, R15.1, U1.IO34, U3.6 (IO34), U5.IRQ/GPIO8 (IRQ)
IO35: J1.18, U1.IO35, U3.7 (IO35)
IO36/SVP: J1.19, U1.SENSOR_VP (SENSR_VP), U3.4 (SENSOR_VP)
IO39/SVN: J1.20, U1.SENSOR_VN (SENSR_VN), U3.5 (SENSOR_VN)
LEDRX: R21.1, U5.GPIO2
LEDRXOK: R23.1, U5.GPIO0
LEDSFD: R22.1, U5.GPIO1
LEDTX: R20.1, U5.GPIO3
unnamed: D1.A, R20.2
unnamed: C9.1, IC1.16 (VPP)
unnamed: C14.1, U2.4 (NC)
unnamed: D3.C, R3.2
unnamed: R8.2, U5.EXTON
unnamed: R13.2, U5.WAKEUP
unnamed: R14.2, U5.RST (RSTN)
unnamed: Q4.1 (B), R12.1
unnamed: Q3.1 (B), R11.1
unnamed: FLASH.2, R10.1
unnamed: D2.A, R21.2
unnamed: D4.A, R22.2
unnamed: D5.A, R23.2
NC: U1.NC0 (NC), U3.32 (NC)
RESET: C12.1, J1.3, Q4.3 (C), R9.1, RST.2, U1.EN, U3.3 (EN)
RTS: IC1.19 (RTS), Q4.2 (E), R11.2
RXD: IC1.21 (TXD), J2.3, U1.RXD0, U3.34 (RXD0)
SD0: U1.SD0, U3.21 (SDO)
SD1: U1.SD1, U3.22 (SD1)
SD2: U1.SD2, U3.17 (SD2)
SD3: U1.SD3, U3.18 (SD3)
TXD: IC1.20 (RXD), J2.4, U1.TXD0, U3.35 (TXD0)
VBUS: C1.1, C2.1, C11.1, D6.+, IC1.8 (VBUS), J3.1 (VCC), R24.2, U2.1 (IN)
VDD5V: C7.1, D6.-, J2.1, U4.3 (IN)

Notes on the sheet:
USB
LEDS
POWER AND FILTERING
USB TO SERIAL CONVERTER
key flash
MakePython ES32 Color LCD V1.0
MTDI
IO34~IO39 input only
Voltage Regulator
VIN: 2.5-6.0V



Board: 2 copper layers, 72.0 x 32.6 mm, 54 parts (27 on the bottom side), 60 nets.

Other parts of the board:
U$1: MAKERFABS_0.3

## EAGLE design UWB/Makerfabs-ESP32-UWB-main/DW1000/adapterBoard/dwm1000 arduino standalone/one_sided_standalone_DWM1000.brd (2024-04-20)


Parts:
C1, C2: CAP_POL3528-KIT; EIA3528-KIT
IC1: V_REG_LM1117SOT223; SOT223
JP1, JP2, JP3, JP4, JP5, JP6, JP7, JP8, JP9, JP10, JP11, JP12, JP13, JP14, JP15, JP16: M01SMD; LUXEON-PAD
R1, R2: RESISTOR0805-RES; 0805
U2: ATMEGA168; TQFP32-08
U$1: DWM1000
X1: USB-MICROB

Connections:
CLK: JP6.P$1, JP10.P$1, U2.17 (PB5(SCK)), U$1.SPICLK
CSN: JP9.P$1, JP13.P$1, U2.14 (PB2(SS/OC1B)), U$1.SPICSN
GND: C1.C (-), C2.C (-), IC1.1 (ADJ), JP16.P$1, R2.1, U2.3 (GND), U2.5 (AGND), U2.21 (GND), U$1.VSS, U$1.VSS.2, U$1.VSS.3, U$1.VSS.4, U$1.VSS.5, X1.GND
IRQ: R2.2, U2.32 (PD2(INT0)), U$1.IRQ/GPIO8 (IRQ)
MISO: JP7.P$1, JP11.P$1, U2.16 (PB4(MISO)), U$1.SPIMISO
MOSI: JP8.P$1, JP12.P$1, U2.15 (PB3(MOSI/OC2)), U$1.SPIMOSI
unnamed: JP1.P$1, U2.7 (PB6(XTAL1/TOSC1))
unnamed: JP2.P$1, U2.8 (PB7(XTAL2/TOSC2))
unnamed: JP3.P$1, R1.1, U2.29 (PC6(/RESET))
unnamed: JP4.P$1, U2.31 (PD1(TXD))
unnamed: JP5.P$1, U2.30 (PD0(RXD))
RESET: U2.13 (PB1(OC1A)), U$1.RST (RSTN)
VCC: C2.A (+), IC1.3 (IN), JP14.P$1, X1.VBUS
VCC3.3: C1.A (+), IC1.2 (OUT), JP15.P$1, R1.2, U2.6 (VCC), U2.18 (AVCC), U2.20 (AREF), U$1.VDD3V3, U$1.VDD3V3.2, U$1.VDDAON


Board: 2 copper layers, 32.4 x 47.4 mm, 24 parts (0 on the bottom side), 14 nets.

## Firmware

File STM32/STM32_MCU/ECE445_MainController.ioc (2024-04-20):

#MicroXplorer Configuration settings - do not modify
CAD.formats=
CAD.pinconfig=
CAD.provider=
File.Version=6
GPIO.groupedBy=Group By Peripherals
KeepUserPlacement=false
Mcu.CPN=STM32F103C8T6TR
Mcu.Family=STM32F1
Mcu.IP0=NVIC
Mcu.IP1=RCC
Mcu.IP2=SPI1
Mcu.IP3=SYS
Mcu.IP4=TIM1
Mcu.IP5=TIM2
Mcu.IP6=TIM3
Mcu.IP7=TIM4
Mcu.IP8=USB
Mcu.IPNb=9
Mcu.Name=STM32F103C(8-B)Tx
Mcu.Package=LQFP48
Mcu.Pin0=PD0-OSC_IN
Mcu.Pin1=PD1-OSC_OUT
Mcu.Pin10=PA8
Mcu.Pin11=PA9
Mcu.Pin12=PA10
Mcu.Pin13=PA11
Mcu.Pin14=PA12
Mcu.Pin15=PA13
Mcu.Pin16=PA14
Mcu.Pin17=PB4
Mcu.Pin18=PB5
Mcu.Pin19=PB6
Mcu.Pin2=PA0-WKUP
Mcu.Pin20=PB7
Mcu.Pin21=PB9
Mcu.Pin22=VP_SYS_VS_Systick
Mcu.Pin23=VP_TIM1_VS_ClockSourceINT
Mcu.Pin3=PA1
Mcu.Pin4=PA2
Mcu.Pin5=PA3
Mcu.Pin6=PA4
Mcu.Pin7=PA5
Mcu.Pin8=PA6
Mcu.Pin9=PA7
Mcu.PinsNb=24
Mcu.ThirdPartyNb=0
Mcu.UserConstants=
Mcu.UserName=STM32F103C8Tx
MxCube.Version=6.11.0
MxDb.Version=DB.6.0.110
NVIC.BusFault_IRQn=true\:0\:0\:false\:false\:true\:false\:false\:false
NVIC.DebugMonitor_IRQn=true\:0\:0\:false\:false\:true\:false\:false\:false
NVIC.ForceEnableDMAVector=true
NVIC.HardFault_IRQn=true\:0\:0\:false\:false\:true\:false\:false\:false
NVIC.MemoryManagement_IRQn=true\:0\:0\:false\:false\:true\:false\:false\:false
NVIC.NonMaskableInt_IRQn=true\:0\:0\:false\:false\:true\:false\:false\:false
NVIC.PendSV_IRQn=true\:0\:0\:false\:false\:true\:false\:false\:false
NVIC.PriorityGroup=NVIC_PRIORITYGROUP_4
NVIC.SVCall_IRQn=true\:0\:0\:false\:false\:true\:false\:false\:false
NVIC.SysTick_IRQn=true\:15\:0\:false\:false\:true\:false\:true\:false
NVIC.UsageFault_IRQn=true\:0\:0\:false\:false\:true\:false\:false\:false
PA0-WKUP.GPIOParameters=GPIO_Label
PA0-WKUP.GPIO_Label=TIM2_CH1_ME1_ChA
PA0-WKUP.Signal=S_TIM2_CH1_ETR
PA1.GPIOParameters=GPIO_Label
PA1.GPIO_Label=TIM2_CH2_ME1_ChB
PA1.Signal=S_TIM2_CH2
PA10.GPIOParameters=GPIO_Label
PA10.GPIO_Label=TIM1_CH3\: PWM Motor 3
PA10.Signal=S_TIM1_CH3
PA11.Mode=Device
PA11.Signal=USB_DM
PA12.Mode=Device
PA12.Signal=USB_DP
PA13.Mode=Serial_Wire
PA13.Signal=SYS_JTMS-SWDIO
PA14.Mode=Serial_Wire
PA14.Signal=SYS_JTCK-SWCLK
PA2.GPIOParameters=GPIO_Speed,GPIO_PuPd,GPIO_Label
PA2.GPIO_Label=SPI1_NSS_RasPi
PA2.GPIO_PuPd=GPIO_PULLUP
PA2.GPIO_Speed=GPIO_SPEED_FREQ_HIGH
PA2.Locked=true
PA2.Signal=GPIO_Output
PA3.GPIOParameters=GPIO_Speed,GPIO_PuPd,GPIO_Label
PA3.GPIO_Label=SPI1_NSS_ESP2
PA3.GPIO_PuPd=GPIO_PULLUP
PA3.GPIO_Speed=GPIO_SPEED_FREQ_HIGH
PA3.Locked=true
PA3.Signal=GPIO_Output
PA4.GPIOParameters=GPIO_Speed,GPIO_PuPd,GPIO_Label
PA4.GPIO_Label=SPI1_NSS_ESP1
PA4.GPIO_PuPd=GPIO_PULLUP
PA4.GPIO_Speed=GPIO_SPEED_FREQ_HIGH
PA4.Locked=true
PA4.Signal=GPIO_Output
PA5.Mode=Full_Duplex_Master
PA5.Signal=SPI1_SCK
PA6.Mode=Full_Duplex_Master
PA6.Signal=SPI1_MISO
PA7.Mode=Full_Duplex_Master
PA7.Signal=SPI1_MOSI
PA8.GPIOParameters=GPIO_Label
PA8.GPIO_Label=TIM1_CH1\: PWM Motor 1
PA8.Signal=S_TIM1_CH1
PA9.GPIOParameters=GPIO_Label
PA9.GPIO_Label=TIM1_CH2\: PWM Motor 2
PA9.Signal=S_TIM1_CH2
PB4.GPIOParameters=GPIO_Label
PB4.GPIO_Label=TIM3_CH1_ME2_ChA
PB4.Signal=S_TIM3_CH1
PB5.GPIOParameters=GPIO_Label
PB5.GPIO_Label=TIM3_CH2_ME2_ChB
PB5.Signal=S_TIM3_CH2
PB6.GPIOParameters=GPIO_Label
PB6.GPIO_Label=TIM4_CH1_ME3_ChA
PB6.Signal=S_TIM4_CH1
PB7.GPIOParameters=GPIO_Label
PB7.GPIO_Label=TIM4_CH2_ME3_ChB
PB7.Signal=S_TIM4_CH2
PB9.GPIOParameters=GPIO_PuPd,GPIO_Label
PB9.GPIO_Label=OR3_LimitSwitches
PB9.GPIO_PuPd=GPIO_PULLDOWN
PB9.Locked=true
PB9.Signal=GPIO_Input
PD0-OSC_IN.Mode=HSE-External-Oscillator
PD0-OSC_IN.Signal=RCC_OSC_IN
PD1-OSC_OUT.Mode=HSE-External-Oscillator
PD1-OSC_OUT.Signal=RCC_OSC_OUT
PinOutPanel.RotationAngle=0
ProjectManager.AskForMigrate=true
ProjectManager.BackupPrevious=false
ProjectManager.CompilerOptimize=6
ProjectManager.ComputerToolchain=false
ProjectManager.CoupleFile=false
ProjectManager.CustomerFirmwarePackage=
ProjectManager.DefaultFWLocation=true
ProjectManager.DeletePrevious=true
ProjectManager.DeviceId=STM32F103C8Tx
ProjectManager.FirmwarePackage=STM32Cube FW_F1 V1.8.5
ProjectManager.FreePins=false
ProjectManager.HalAssertFull=false
ProjectManager.HeapSize=0x200
ProjectManager.KeepUserCode=true
ProjectManager.LastFirmware=true
ProjectManager.LibraryCopy=1
ProjectManager.MainLocation=Core/Src
ProjectManager.NoMain=false
ProjectManager.PreviousToolchain=
ProjectManager.ProjectBuild=false
ProjectManager.ProjectFileName=ECE445_MainController.ioc
ProjectManager.ProjectName=ECE445_MainController
ProjectManager.ProjectStructure=
ProjectManager.RegisterCallBack=
ProjectManager.StackSize=0x400
ProjectManager.TargetToolchain=STM32CubeIDE
ProjectManager.ToolChainLocation=
ProjectManager.UAScriptAfterPath=
ProjectManager.UAScriptBeforePath=
ProjectManager.UnderRoot=true
ProjectManager.functionlistsort=1-SystemClock_Config-RCC-false-HAL-false,2-MX_GPIO_Init-GPIO-false-HAL-true,3-MX_SPI1_Init-SPI1-false-HAL-true,4-MX_TIM1_Init-TIM1-false-HAL-true,5-MX_TIM2_Init-TIM2-false-HAL-true,6-MX_TIM3_Init-TIM3-false-HAL-true,7-MX_TIM4_Init-TIM4-false-HAL-true
RCC.ADCFreqValue=24000000
RCC.AHBFreq_Value=48000000
RCC.APB1CLKDivider=RCC_HCLK_DIV2
RCC.APB1Freq_Value=24000000
RCC.APB1TimFreq_Value=48000000
RCC.APB2Freq_Value=48000000
RCC.APB2TimFreq_Value=48000000
RCC.FCLKCortexFreq_Value=48000000
RCC.FamilyName=M
RCC.HCLKFreq_Value=48000000
RCC.IPParameters=ADCFreqValue,AHBFreq_Value,APB1CLKDivider,APB1Freq_Value,APB1TimFreq_Value,APB2Freq_Value,APB2TimFreq_Value,FCLKCortexFreq_Value,FamilyName,HCLKFreq_Value,MCOFreq_Value,PLLCLKFreq_Value,PLLMCOFreq_Value,PLLMUL,SYSCLKFreq_VALUE,SYSCLKSource,TimSysFreq_Value,USBFreq_Value,VCOOutput2Freq_Value
RCC.MCOFreq_Value=48000000
RCC.PLLCLKFreq_Value=48000000
RCC.PLLMCOFreq_Value=24000000
RCC.PLLMUL=RCC_PLL_MUL6
RCC.SYSCLKFreq_VALUE=48000000
RCC.SYSCLKSource=RCC_SYSCLKSOURCE_PLLCLK
RCC.TimSysFreq_Value=48000000
RCC.USBFreq_Value=48000000
RCC.VCOOutput2Freq_Value=8000000
SH.S_TIM1_CH1.0=TIM1_CH1,PWM Generation1 CH1
SH.S_TIM1_CH1.ConfNb=1
SH.S_TIM1_CH2.0=TIM1_CH2,PWM Generation2 CH2
SH.S_TIM1_CH2.ConfNb=1
SH.S_TIM1_CH3.0=TIM1_CH3,PWM Generation3 CH3
SH.S_TIM1_CH3.ConfNb=1
SH.S_TIM2_CH1_ETR.0=TIM2_CH1,Encoder_Interface
SH.S_TIM2_CH1_ETR.ConfNb=1
SH.S_TIM2_CH2.0=TIM2_CH2,Encoder_Interface
SH.S_TIM2_CH2.ConfNb=1
SH.S_TIM3_CH1.0=TIM3_CH1,Encoder_Interface
SH.S_TIM3_CH1.ConfNb=1
SH.S_TIM3_CH2.0=TIM3_CH2,Encoder_Interface
SH.S_TIM3_CH2.ConfNb=1
SH.S_TIM4_CH1.0=TIM4_CH1,Encoder_Interface
SH.S_TIM4_CH1.ConfNb=1
SH.S_TIM4_CH2.0=TIM4_CH2,Encoder_Interface
SH.S_TIM4_CH2.ConfNb=1
SPI1.BaudRatePrescaler=SPI_BAUDRATEPRESCALER_2
SPI1.CalculateBaudRate=24.0 MBits/s
SPI1.Direction=SPI_DIRECTION_2LINES
SPI1.IPParameters=VirtualType,Mode,Direction,CalculateBaudRate,BaudRatePrescaler
SPI1.Mode=SPI_MODE_MASTER
SPI1.VirtualType=VM_MASTER
TIM1.Channel-PWM\ Generation1\ CH1=TIM_CHANNEL_1
TIM1.Channel-PWM\ Generation2\ CH2=TIM_CHANNEL_2
TIM1.Channel-PWM\ Generation3\ CH3=TIM_CHANNEL_3
TIM1.IPParameters=Channel-PWM Generation1 CH1,Prescaler,Period,Channel-PWM Generation2 CH2,Channel-PWM Generation3 CH3
TIM1.Period=100-1
TIM1.Prescaler=72-1
VP_SYS_VS_Systick.Mode=SysTick
VP_SYS_VS_Systick.Signal=SYS_VS_Systick
VP_TIM1_VS_ClockSourceINT.Mode=Internal
VP_TIM1_VS_ClockSourceINT.Signal=TIM1_VS_ClockSourceINT
board=custom
isbadioc=true

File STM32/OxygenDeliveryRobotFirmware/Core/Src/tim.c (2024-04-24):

/* USER CODE BEGIN Header */
/**
  ******************************************************************************
  * @file    tim.c
  * @brief   This file provides code for the configuration
  *          of the TIM instances.
  ******************************************************************************
  * @attention
  *
  * Copyright (c) 2024 STMicroelectronics.
  * All rights reserved.
  *
  * This software is licensed under terms that can be found in the LICENSE file
  * in the root directory of this software component.
  * If no LICENSE file comes with this software, it is provided AS-IS.
  *
  ******************************************************************************
  */
/* USER CODE END Header */
/* Includes ------------------------------------------------------------------*/
#include "tim.h"

/* USER CODE BEGIN 0 */

/* USER CODE END 0 */

TIM_HandleTypeDef htim1;
TIM_HandleTypeDef htim2;
TIM_HandleTypeDef htim3;
TIM_HandleTypeDef htim4;

/* TIM1 init function */
void MX_TIM1_Init(void)
{

  /* USER CODE BEGIN TIM1_Init 0 */

  /* USER CODE END TIM1_Init 0 */

  TIM_ClockConfigTypeDef sClockSourceConfig = {0};
  TIM_MasterConfigTypeDef sMasterConfig = {0};
  TIM_OC_InitTypeDef sConfigOC = {0};
  TIM_BreakDeadTimeConfigTypeDef sBreakDeadTimeConfig = {0};

  /* USER CODE BEGIN TIM1_Init 1 */

  /* USER CODE END TIM1_Init 1 */
  htim1.Instance = TIM1;
  htim1.Init.Prescaler = 72-1;
  htim1.Init.CounterMode = TIM_COUNTERMODE_UP;
  htim1.Init.Period = 20000-1;
  htim1.Init.ClockDivision = TIM_CLOCKDIVISION_DIV1;
  htim1.Init.RepetitionCounter = 0;
  htim1.Init.AutoReloadPreload = TIM_AUTORELOAD_PRELOAD_DISABLE;
  if (HAL_TIM_Base_Init(&htim1) != HAL_OK)
  {
    Error_Handler();
  }
  sClockSourceConfig.ClockSource = TIM_CLOCKSOURCE_INTERNAL;
  if (HAL_TIM_ConfigClockSource(&htim1, &sClockSourceConfig) != HAL_OK)
  {
    Error_Handler();
  }
  if (HAL_TIM_PWM_Init(&htim1) != HAL_OK)
  {
    Error_Handler();
  }
  sMasterConfig.MasterOutputTrigger = TIM_TRGO_RESET;
  sMasterConfig.MasterSlaveMode = TIM_MASTERSLAVEMODE_DISABLE;
  if (HAL_TIMEx_MasterConfigSynchronization(&htim1, &sMasterConfig) != HAL_OK)
  {
    Error_Handler();
  }
  sConfigOC.OCMode = TIM_OCMODE_PWM1;
  sConfigOC.Pulse = 6000;
  sConfigOC.OCPolarity = TIM_OCPOLARITY_HIGH;
  sConfigOC.OCNPolarity = TIM_OCNPOLARITY_HIGH;
  sConfigOC.OCFastMode = TIM_OCFAST_DISABLE;
  sConfigOC.OCIdleState = TIM_OCIDLESTATE_RESET;
  sConfigOC.OCNIdleState = TIM_OCNIDLESTATE_RESET;
  if (HAL_TIM_PWM_ConfigChannel(&htim1, &sConfigOC, TIM_CHANNEL_1) != HAL_OK)
  {
    Error_Handler();
  }
  sConfigOC.Pulse = 3000;
  if (HAL_TIM_PWM_ConfigChannel(&htim1, &sConfigOC, TIM_CHANNEL_2) != HAL_OK)
  {
    Error_Handler();
  }
  if (HAL_TIM_PWM_ConfigChannel(&htim1, &sConfigOC, TIM_CHANNEL_3) != HAL_OK)
  {
    Error_Handler();
  }
  sBreakDeadTimeConfig.OffStateRunMode = TIM_OSSR_DISABLE;
  sBreakDeadTimeConfig.OffStateIDLEMode = TIM_OSSI_DISABLE;
  sBreakDeadTimeConfig.LockLevel = TIM_LOCKLEVEL_OFF;
  sBreakDeadTimeConfig.DeadTime = 0;
  sBreakDeadTimeConfig.BreakState = TIM_BREAK_DISABLE;
  sBreakDeadTimeConfig.BreakPolarity = TIM_BREAKPOLARITY_HIGH;
  sBreakDeadTimeConfig.AutomaticOutput = TIM_AUTOMATICOUTPUT_DISABLE;
  if (HAL_TIMEx_ConfigBreakDeadTime(&htim1, &sBreakDeadTimeConfig) != HAL_OK)
  {
    Error_Handler();
  }
  /* USER CODE BEGIN TIM1_Init 2 */

  /* USER CODE END TIM1_Init 2 */
  HAL_TIM_MspPostInit(&htim1);

}
/* TIM2 init function */
void MX_TIM2_Init(void)
{

  /* USER CODE BEGIN TIM2_Init 0 */

  /* USER CODE END TIM2_Init 0 */

  TIM_Encoder_InitTypeDef sConfig = {0};
  TIM_MasterConfigTypeDef sMasterConfig = {0};

  /* USER CODE BEGIN TIM2_Init 1 */

  /* USER CODE END TIM2_Init 1 */
  htim2.Instance = TIM2;
  htim2.Init.Prescaler = 0;
  htim2.Init.CounterMode = TIM_COUNTERMODE_UP;
  htim2.Init.Period = 65535;
  htim2.Init.ClockDivision = TIM_CLOCKDIVISION_DIV1;
  htim2.Init.AutoReloadPreload = TIM_AUTORELOAD_PRELOAD_DISABLE;
  sConfig.EncoderMode = TIM_ENCODERMODE_TI12;
  sConfig.IC1Polarity = TIM_ICPOLARITY_FALLING;
  sConfig.IC1Selection = TIM_ICSELECTION_DIRECTTI;
  sConfig.IC1Prescaler = TIM_ICPSC_DIV1;
  sConfig.IC1Filter = 0;
  sConfig.IC2Polarity = TIM_ICPOLARITY_FALLING;
  sConfig.IC2Selection = TIM_ICSELECTION_DIRECTTI;
  sConfig.IC2Prescaler = TIM_ICPSC_DIV1;
  sConfig.IC2Filter = 0;
  if (HAL_TIM_Encoder_Init(&htim2, &sConfig) != HAL_OK)
  {
    Error_Handler();
  }
  sMasterConfig.MasterOutputTrigger = TIM_TRGO_RESET;
  sMasterConfig.MasterSlaveMode = TIM_MASTERSLAVEMODE_DISABLE;
  if (HAL_TIMEx_MasterConfigSynchronization(&htim2, &sMasterConfig) != HAL_OK)
  {
    Error_Handler();
  }
  /* USER CODE BEGIN TIM2_Init 2 */
//  HAL_TIM_Base_Start_IT(&htim2); // Start the interrupt
//  HAL_TIM_Base_Start(&htim2); // Start the timer
  /* USER CODE END TIM2_Init 2 */

}
/* TIM3 init function */
void MX_TIM3_Init(void)
{

  /* USER CODE BEGIN TIM3_Init 0 */

  /* USER CODE END TIM3_Init 0 */

  TIM_Encoder_InitTypeDef sConfig = {0};
  TIM_MasterConfigTypeDef sMasterConfig = {0};

  /* USER CODE BEGIN TIM3_Init 1 */

  /* USER CODE END TIM3_Init 1 */
  htim3.Instance = TIM3;
  htim3.Init.Prescaler = 0;
  htim3.Init.CounterMode = TIM_COUNTERMODE_UP;
  htim3.Init.Period = 65535;
  htim3.Init.ClockDivision = TIM_CLOCKDIVISION_DIV1;
  htim3.Init.AutoReloadPreload = TIM_AUTORELOAD_PRELOAD_DISABLE;
  sConfig.EncoderMode = TIM_ENCODERMODE_TI12;
  sConfig.IC1Polarity = TIM_ICPOLARITY_FALLING;
  sConfig.IC1Selection = TIM_ICSELECTION_DIRECTTI;
  sConfig.IC1Prescaler = TIM_ICPSC_DIV1;
  sConfig.IC1Filter = 0;
  sConfig.IC2Polarity = TIM_ICPOLARITY_FALLING;
  sConfig.IC2Selection = TIM_ICSELECTION_DIRECTTI;
  sConfig.IC2Prescaler = TIM_ICPSC_DIV1;
  sConfig.IC2Filter = 0;
  if (HAL_TIM_Encoder_Init(&htim3, &sConfig) != HAL_OK)
  {
    Error_Handler();
  }
  sMasterConfig.MasterOutputTrigger = TIM_TRGO_RESET;
  sMasterConfig.MasterSlaveMode = TIM_MASTERSLAVEMODE_DISABLE;
  if (HAL_TIMEx_MasterConfigSynchronization(&htim3, &sMasterConfig) != HAL_OK)
  {
    Error_Handler();
  }
  /* USER CODE BEGIN TIM3_Init 2 */

  /* USER CODE END TIM3_Init 2 */

}
/* TIM4 init function */
void MX_TIM4_Init(void)
{

  /* USER CODE BEGIN TIM4_Init 0 */

  /* USER CODE END TIM4_Init 0 */

  TIM_Encoder_InitTypeDef sConfig = {0};
  TIM_MasterConfigTypeDef sMasterConfig = {0};

  /* USER CODE BEGIN TIM4_Init 1 */

  /* USER CODE END TIM4_Init 1 */
  htim4.Instance = TIM4;
  htim4.Init.Prescaler = 0;
  htim4.Init.CounterMode = TIM_COUNTERMODE_UP;
  htim4.Init.Period = 65535;
  htim4.Init.ClockDivision = TIM_CLOCKDIVISION_DIV1;
  htim4.Init.AutoReloadPreload = TIM_AUTORELOAD_PRELOAD_DISABLE;
  sConfig.EncoderMode = TIM_ENCODERMODE_TI12;
  sConfig.IC1Polarity = TIM_ICPOLARITY_FALLING;
  sConfig.IC1Selection = TIM_ICSELECTION_DIRECTTI;
  sConfig.IC1Prescaler = TIM_ICPSC_DIV1;
  sConfig.IC1Filter = 0;
  sConfig.IC2Polarity = TIM_ICPOLARITY_FALLING;
  sConfig.IC2Selection = TIM_ICSELECTION_DIRECTTI;
  sConfig.IC2Prescaler = TIM_ICPSC_DIV1;
  sConfig.IC2Filter = 0;
  if (HAL_TIM_Encoder_Init(&htim4, &sConfig) != HAL_OK)
  {
    Error_Handler();
  }
  sMasterConfig.MasterOutputTrigger = TIM_TRGO_RESET;
  sMasterConfig.MasterSlaveMode = TIM_MASTERSLAVEMODE_DISABLE;
  if (HAL_TIMEx_MasterConfigSynchronization(&htim4, &sMasterConfig) != HAL_OK)
  {
    Error_Handler();
  }
  /* USER CODE BEGIN TIM4_Init 2 */

  /* USER CODE END TIM4_Init 2 */

}

void HAL_TIM_Base_MspInit(TIM_HandleTypeDef* tim_baseHandle)
{

  if(tim_baseHandle->Instance==TIM1)
  {
  /* USER CODE BEGIN TIM1_MspInit 0 */

  /* USER CODE END TIM1_MspInit 0 */
    /* TIM1 clock enable */
    __HAL_RCC_TIM1_CLK_ENABLE();
  /* USER CODE BEGIN TIM1_MspInit 1 */

  /* USER CODE END TIM1_MspInit 1 */
  }
}
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

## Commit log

2024-02-18 Create Motor Research - Sheet1.pdf
    Motor Research
2024-02-19 Update AidanProgress.txt
    Started drivetrain portion of pcb research
2024-02-20 Motor Research Update
2024-02-29 Adding PCB progress with Power subsection and adding STM32
    [MainBoard.kicad_pcb, MainBoard.kicad_sch, power.kicad_sch]
2024-02-29 adding some misc images and files
    [PartOrder1.xlsx]
2024-03-01 updating pcb
    [MainBoard.kicad_sch, power.kicad_sch]
2024-03-01 updating progress
    [MainBoard.kicad_sch, power.kicad_sch]
2024-03-04 5v 1.2A buck converter
2024-03-04 3.3v .15A buck converter
2024-03-04 adding nazar's work onto new branch
    [power.kicad_sch]
2024-03-04 updating power schematics, and power lines
    [3v3BuckConverter.kicad_sch, 5V1.2ABuckConverter.kicad_sch, 5V3ABuckConverter.kicad_sch, MainBoard.kicad_sch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]
2024-03-05 passed ERC in schematic
    [3v3BuckConverter.kicad_sch, 5V1.2ABuckConverter.kicad_sch, 5V3ABuckConverter.kicad_sch, LimitSwitchOR.kicad_sch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]
2024-03-05 began placing components - motor connectors, 12V in, mounting holes
    [LimitSwitchOR.kicad_sch, MainBoard.kicad_pcb, MainBoard.kicad_sch, power.kicad_sch]
2024-03-05 Placed Buck Converters and changed inductors to 1008
    [3v3BuckConverter.kicad_sch, 5V1.2ABuckConverter.kicad_sch, 5V3ABuckConverter.kicad_sch, MainBoard.kicad_pcb]
2024-03-05 updated pcb schematic
    [MainBoard.kicad_pcb]
2024-03-05 final layout v1 - unconnected
    [MainBoard.kicad_pcb, MainBoard.kicad_sch, power.kicad_sch]
2024-03-05 board routed, just need to increase track widths for power lines
    [MainBoard.kicad_pcb]
2024-03-05 Updated PCB and passed DRC
    [MainBoard.kicad_pcb]
2024-03-05 Created Gerber Files
    [MainBoard-B_Cu.gbr, MainBoard-B_Mask.gbr, MainBoard-B_Paste.gbr, MainBoard-B_Silkscreen.gbr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]
2024-03-18 Exported BOM
    [MainBoard_BOM_v1.csv]
2024-03-18 Updating main PCB for version 1.1
    [MainBoard.kicad_pcb]
2024-03-18 updating v1.1 with chamfered traces
    [MainBoard.kicad_pcb]
2024-03-19 updating PCB with new components and proper footprints, still need to fix footprint matching issue.
    [5442170.stp, 5V3ABuckConverter.kicad_sch, MainBoard-B_Cu.gbr, MainBoard-B_Mask.gbr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]
2024-03-19 fixing some right angles in board
    [MainBoard.kicad_pcb]
2024-03-19 v1.1 of MainBoard complete - PCBWay DRC Passes
    [5V3ABuckConverter.kicad_sch, MainBoard-B_Cu.gbr, MainBoard-B_Mask.gbr, MainBoard-B_Paste.gbr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]
2024-03-19 organizing Rutvik progress section
    [PartOrder1.xlsx]
2024-03-22 Adding Manufacturer OWB Test Code
    [ESP32 UWB Pro with Display v1.2.brd, ESP32 UWB Pro with Display v1.2.sch, ESP32 UWB v1.0.brd, ESP32 UWB v1.0.sch]
2024-03-26 updating 3d printing files and progress report - rutvik
    [LimitSwitchConnector.stl, LimitSwitchScrewTerminal.stl]
2024-03-28 adding 3d printing stl files for limit switch bumper
    [LimitSwitchConnectorv2.stl, LimitSwitchScrewTerminalv2.stl, LimitSwitchScrewTerminalv3.stl]
2024-04-01 Updated progress and uploaded bumper cad file
    [Bumper v15.f3d, MainBoard.step]
2024-04-01 pushing 3d printing stl files
    [LimitSwitchScrewTerminalv4.stl, LimitSwitchScrewTerminalv5.stl]
2024-04-02 starting stm32cube pin mapping
    [MainBoard.kicad_sch]
2024-04-02 adding all stm32 projects
2024-04-03 adding board v2 progress
    [3v3BuckConverter.kicad_sch, MainBoard.kicad_sch, MainBoardv2.kicad_pcb, MainBoardv2.kicad_sch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]
2024-04-04 Updating progress on board v2
    [B4B-XH-A.step, LimitSwitchOR.kicad_sch, MainBoardv2.kicad_sch]
2024-04-05 updating main board v2 progress
    [IHLP3232DZ.stl, LimitSwitchOR.kicad_sch, MainBoardv2.kicad_sch, PW0014A.stl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]
2024-04-05 updating main board v2 with motor power conns
    [MainBoard.kicad_sch, MainBoardv2.kicad_sch, PWM.kicad_sch]
2024-04-05 updating progress for board v2
    [MainBoardv2.kicad_sch, Motors.kicad_sch, PWM.kicad_sch]
2024-04-05 board v2 passing ERC in schematic
    [MainBoardv2.kicad_sch, Motors.kicad_sch, PWM.kicad_sch]
2024-04-05 footprints all assigned for board v2
    [10118192-0002LF.step, MainBoardv2.kicad_sch, Motors.kicad_sch, PWM.kicad_sch]
2024-04-07 Updated part assignments on board for digikey order
    [BOM_MainBoardv2.csv, MainBoardv2.kicad_sch, Motors.kicad_sch, PWM.kicad_sch]
2024-04-07 pushing progress on mainboard v2 layout
    [1017521.step, 5002.step, 5003.step, GF-161-0005_3D Model.stp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]
2024-04-08 Main Board v2 Rough component layout complete
    [MainBoardv2.kicad_pcb, MainBoardv2.kicad_sch, Motors.kicad_sch, PWM.kicad_sch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]
2024-04-09 updating layout progress, adding limit switch extra circuitry
    [LimitSwitch.kicad_sch, MainBoardv2.kicad_pcb, MainBoardv2.kicad_sch, Motors.kicad_sch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]
2024-04-09 PCB laid out & passes DRC
    [LimitSwitch.kicad_sch, MainBoardv2.kicad_pcb, MainBoardv2.kicad_sch]
2024-04-09 main board v2 sent to fab
    [BOM_MainBoardv2.csv, LimitSwitch.kicad_sch, LimitSwitchOR.kicad_sch, MainBoardv2-B_Cu.gbr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]
2024-04-17 UWB files update
    [AdapterBoardTestBed.fzz, adapterBoard.fzz, adapterBoard_contour.gm1, adapterBoard_copperBottom.gbl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]
2024-04-19 repo clean up, orgainizing stm32 folders, deleting mainbaordv2.1
    deleting mainbaordv2.1 as it was never completed. too many misc stm32 folders, consolidated for orgaization
    [BOM_MainBoardv2.csv, LimitSwitch.kicad_sch, LimitSwitchOR.kicad_sch, MainBoardv2_1.kicad_pcb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]
2024-04-20 adding 3d printing files for bumper
    [LimitSwitchBody3_v5.stl, LimitSwitchBumper.stl, LimitSwitchBumperInterlocking1.stl, LimitSwitchInterlocking2.stl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]
2024-04-23 adding limit switch update and oxygen tank standoff
    [MainBodyLimitSwitch.stl, OxygenTankStandoff.stl]
2024-04-23 updating standoff
    [OxygenTankStandoff.stl]
2024-04-23 updating firmware for delivery robot, scaling motor speed with map
2024-04-23 misc files for STM32 old directory
2024-04-24 adding battery housing 3d print file
    [BatteryHousing.stl]
2024-04-26 adding printout files
2024-04-29 adding battery housing creality file
2024-05-02 Pushing final report files
    [AdapterBoardTestBed.fzz, ESP32 UWB Pro with Display v1.2.brd, ESP32 UWB Pro with Display v1.2.sch, ESP32 UWB v1.0.brd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]

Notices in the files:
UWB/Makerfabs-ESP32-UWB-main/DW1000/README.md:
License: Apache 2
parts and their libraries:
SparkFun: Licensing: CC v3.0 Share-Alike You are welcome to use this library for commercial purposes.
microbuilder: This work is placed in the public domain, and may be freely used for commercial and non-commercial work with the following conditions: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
